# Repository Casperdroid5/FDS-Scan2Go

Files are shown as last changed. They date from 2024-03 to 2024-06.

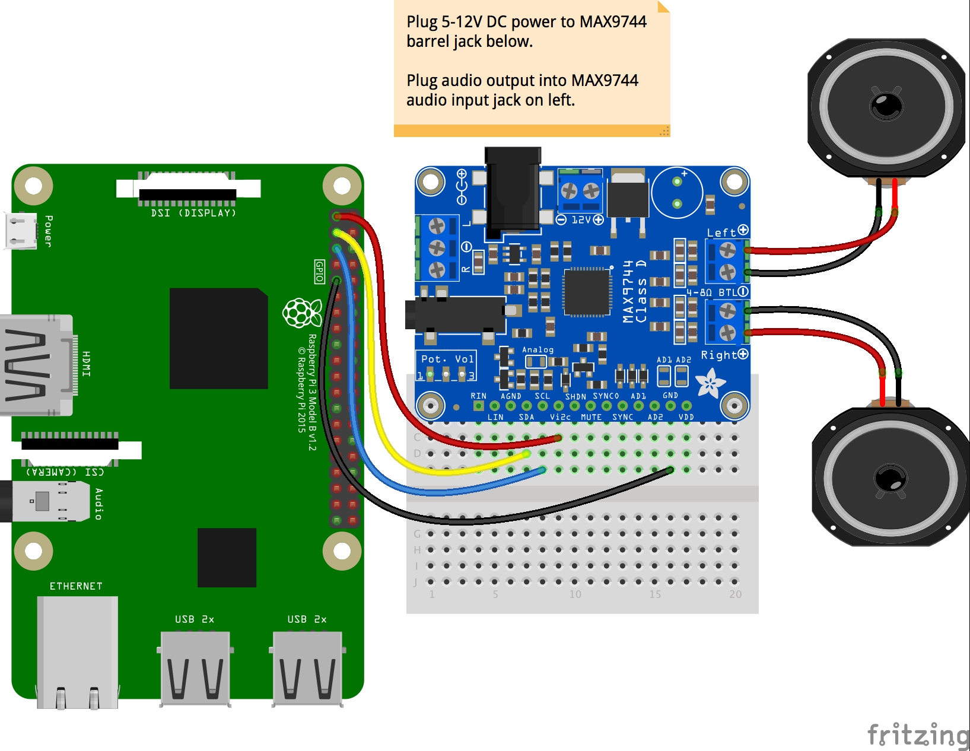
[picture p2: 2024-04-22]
Hardware/Datasheets e.d/adafruit_products_raspi_max9744_i2c_bb.jpg

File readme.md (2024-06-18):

# FDS-Scan2Go

## Overview
The Ferrous Metal Detection Gate (FDS) is a sophisticated system designed to enhance safety for MRI room access by detecting ferrous metals. This system utilizes a Raspberry Pi Pico and Raspberry Pi 5 to facilitate communication with various sensors, providing both auditory and visual feedback to the user.

## Table of Contents
- [Features](#features)
- [Hardware Requirements](#hardware-requirements)
- [Software Setup](#software-setup)
- [Installation](#installation)
  - [Raspberry Pi Pico](#raspberry-pi-pico)
  - [Raspberry Pi 5](#raspberry-pi-5)
- [Usage](#usage)
- [Contributing](#contributing)
- [License](#license)

## Features
- Utilizes a ferrous metal detector for metal detection
- Provides auditory and visual feedback to the user
- Employs both Raspberry Pi Pico and Raspberry Pi 5
- Communicates with multiple sensors for enhanced detection accuracy

## Hardware Requirements
### Raspberry Pi Pico
- All the wanted peripherals (buttons, sensors etc.)
- Micro usb cable (ensure it has data wires)

### Raspberry Pi 5
- Raspberry Pi 25W, power supply
- USB to 3.5mm audio adapter
- Display/monitor for imageoutput
- MicroHDMI to HDMI adapter 

## Software Setup
### Prerequisites
- Python 3.12 or higher
- Required Python libraries (listed in `requirements_rpi5.txt` for Raspberry Pi 5)
- MicroPython libraries for Raspberry Pi Pico (listed in `requirements_pico.txt`)

## Installation
### Raspberry Pi Pico

1. **Install Dependencies**
   Since the Pico runs on MicroPython for this project, you'll need to upload the required libraries manually or use a tool like `mpremote`.

   ```sh
   mpremote mip install micropython-neopixel micropython-machine micropython-time micropython-i2c micropython-uart
   ```

2. **Upload Scripts to Pico**
   Upload the relevant `.py` files to the Pico:
   ```sh
   mpremote fs cp hardware_s2g.py :hardware_s2g.py
   mpremote fs cp system_utils.py :system_utils.py
   mpremote fs cp main.py :main.py
   ```

### Raspberry Pi 5
1. **Prepare MicroSD Card**
   Install Raspbian 64-bit (with desktop) on a 32GB MicroSD card (using Raspberry Pi Imager, for example). Once installed, boot the Raspberry Pi 5, connect it to the internet, and open a terminal with root permissions.

2. **Install Python Dependencies**
   ```sh
   pip install -r requirements_rpi5.txt
   ```

3. **Install System Dependencies**
   ```sh
   sudo apt-get update
   sudo apt-get install feh vlc
   ```

4. **Run the Application**
   Navigate to the project directory and start the main script:
   ```sh
   python main.py
   ```

## Usage
1. **Connect the Raspberry Pi Pico and Raspberry Pi 5 via a MicroUSB cable.**
2. **Start the `main.py` script on the Raspberry Pi 5.**
3. The system will initialize, and the sensors will begin to monitor for ferrous metals. The NeoPixel LEDs and the display will provide feedback based on the detection status.

## Contributing
We welcome contributions to the FDS-Scan2Go project. If you would like to contribute, please fork the repository and submit a pull request. 

If you would like to emplement this code into your own project, ensure to give credit to the original author and mention any significant changes or improvements.

## Disclaimer
This project is licensed under the MIT License. See the [DISCLAIMER](/Software/DISCLAIMER.md) file for more details.

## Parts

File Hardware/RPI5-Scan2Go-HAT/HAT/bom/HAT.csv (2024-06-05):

'Reference' | 'Value' | 'Datasheet' | 'Footprint' | 'Qty' | 'Mouser' | 'Description' | 'Farnell'
'C1' | '0.1uF' | 'https://nl.mouser.com/datasheet/2/40/cx5r-2835979.pdf' | 'Capacitor_SMD:C_1206_3216Metric_Pad1.33x1.80mm_HandSolder' | '1' | '581-12066D104KAT4A ' | 'Unpolarized capacitor' | ''
'D1' | '5.0V' | 'https://www.bourns.com/docs/product-datasheets/smbj.pdf?sfvrsn=34552159_17' | 'SamacSys_Parts:DIOM5436X261N' | '1' | '652-SMBJ26A ' | '' | ''
'D2' | 'WS2812B' | 'https://cdn-shop.adafruit.com/datasheets/WS2812B.pdf' | 'LED_SMD:LED_WS2812B_PLCC4_5.0x5.0mm_P3.2mm' | '1' | ' 474-COM-16346 ' | 'RGB LED with integrated controller' | ''
'F1' | '5 A' | 'https://nl.mouser.com/datasheet/2/54/Bourns_01_26_2024_SF_1206S_R_Datasheet-3398014.pdf' | 'Fuse:Fuse_2010_5025Metric_Pad1.52x2.65mm_HandSolder' | '1' | '652-SF-1206HH1000R-2 ' | '' | ''
'IC1' | 'MC14043BDR2G' | 'https://www.onsemi.com/pub/Collateral/MC14043B-D.PDF' | 'SamacSys_Parts:SOIC127P600X175-16N' | '1' | '863-MC14043BDR2G' | 'ON SEMICONDUCTOR - MC14043BDR2G - SR-LATCH, QUAD, TRI-STATE, SOIC-16' | ''
'J1' | 'RPi_GPIO' | 'https://nl.mouser.com/datasheet/2/813/12313-1074847.pdf' | '_custom:Pin_Header_Straight_2x20' | '1' | '474-PRT-14017 ' | '' | ''
'J2' | 'Conn_01x02_Socket' | '~' | 'Connector_JST:JST_EH_B2B-EH-A_1x02_P2.50mm_Vertical' | '1' | '' | 'Generic connector, single row, 01x02, script generated' | ' 2399159 '
'J3' | 'Conn_01x14_Socket' | '~' | 'Connector_PinSocket_2.54mm:PinSocket_1x14_P2.54mm_Vertical' | '1' | '' | 'Generic connector, single row, 01x14, script generated' | ''
'J4' | 'Conn_01x03_Socket' | '~' | 'Connector_JST:JST_EH_B3B-EH-A_1x03_P2.50mm_Vertical' | '1' | '' | 'Generic connector, single row, 01x03, script generated' | ' 2399161 '
'J5' | 'Conn_01x03_Socket' | '~' | 'Connector_JST:JST_EH_B3B-EH-A_1x03_P2.50mm_Vertical' | '1' | '' | 'Generic connector, single row, 01x03, script generated' | ' 2399161 '
'J6' | 'Conn_01x03_Socket' | '~' | 'Connector_JST:JST_EH_B3B-EH-A_1x03_P2.50mm_Vertical' | '1' | '' | 'Generic connector, single row, 01x03, script generated' | ' 2399161 '
'J7' | 'Conn_01x04_Socket' | '~' | 'Connector_JST:JST_EH_B4B-EH-A_1x04_P2.50mm_Vertical' | '1' | '' | 'Generic connector, single row, 01x04, script generated' | '1830714'
'J8' | 'Conn_01x02_Socket' | '~' | 'Connector_JST:JST_EH_B2B-EH-A_1x02_P2.50mm_Vertical' | '1' | '' | 'Generic connector, single row, 01x02, script generated' | ' 2399159 '
'J9' | 'Conn_01x02_Socket' | '~' | 'Connector_JST:JST_EH_B2B-EH-A_1x02_P2.50mm_Vertical' | '1' | '' | 'Generic connector, single row, 01x02, script generated' | ' 2399159 '
'J10' | 'Conn_01x02_Socket' | '~' | 'Connector_JST:JST_EH_B2B-EH-A_1x02_P2.50mm_Vertical' | '1' | '' | 'Generic connector, single row, 01x02, script generated' | ' 2399159 '
'J12' | 'Conn_01x02_Socket' | '~' | 'Connector_JST:JST_EH_B2B-EH-A_1x02_P2.50mm_Vertical' | '1' | '' | 'Generic connector, single row, 01x02, script generated' | ' 2399159 '
'J13' | 'Conn_01x02_Socket' | '~' | 'Connector_JST:JST_EH_B2B-EH-A_1x02_P2.50mm_Vertical' | '1' | '' | 'Generic connector, single row, 01x02, script generated' | ' 2399159 '
'J14' | 'Conn_01x02_Socket' | '~' | 'Connector_JST:JST_EH_B2B-EH-A_1x02_P2.50mm_Vertical' | '1' | '' | 'Generic connector, single row, 01x02, script generated' | ' 2399159 '
'J15' | 'Jack-DC 5V' | 'https://nl.farnell.com/cliff-electronic-components/fcr681466p/dc-barrel-conn-jack-2-1mm-2-5mm/dp/2759202' | 'Connector_BarrelJack:BarrelJack_Wuerth_6941xx301002' | '1' | '' | '' | 'FCR681466P'
'J16' | 'Conn_01x03_Socket' | '~' | 'Connector_JST:JST_EH_B3B-EH-A_1x03_P2.50mm_Vertical' | '1' | '' | 'Generic connector, single row, 01x03, script generated' | ' 2399161 '
'J18' | 'Conn_01x02_Socket' | '~' | 'Connector_JST:JST_EH_B2B-EH-A_1x02_P2.50mm_Vertical' | '1' | '' | 'Generic connector, single row, 01x02, script generated' | ' 2399159 '
'J19' | 'Conn_01x02_Socket' | '~' | 'Connector_JST:JST_EH_B2B-EH-A_1x02_P2.50mm_Vertical' | '1' | '' | 'Generic connector, single row, 01x02, script generated' | ' 2399159 '
'J20' | 'Conn_01x05_Socket' | '~' | 'Connector_JST:JST_EH_B5B-EH-A_1x05_P2.50mm_Vertical' | '1' | '' | 'Generic connector, single row, 01x05, script generated' | '1830716 '
'J21' | 'Conn_01x05_Socket' | '~' | 'Connector_JST:JST_EH_B5B-EH-A_1x05_P2.50mm_Vertical' | '1' | '' | 'Generic connector, single row, 01x05, script generated' | '1830716 '
'J22' | 'Conn_01x02_Socket' | '~' | 'Connector_JST:JST_EH_B2B-EH-A_1x02_P2.50mm_Vertical' | '1' | '' | 'Generic connector, single row, 01x02, script generated' | ' 2399159 '
'J23' | 'Conn_01x04_Socket' | '~' | 'Connector_JST:JST_EH_B4B-EH-A_1x04_P2.50mm_Vertical' | '1' | '' | 'Generic connector, single row, 01x04, script generated' | '1830714'
'J24' | 'Conn_01x02_Socket' | '~' | 'Connector_JST:JST_EH_B2B-EH-A_1x02_P2.50mm_Vertical' | '1' | '' | 'Generic connector, single row, 01x02, script generated' | ' 2399159 '
'JP1' | 'Jumper_2_Open' | '~' | 'Jumper:SolderJumper-2_P1.3mm_Open_TrianglePad1.0x1.5mm' | '1' | '' | 'Jumper, 2-pole, open' | ''
'JP2' | 'Jumper_2_Open' | '~' | 'Jumper:SolderJumper-2_P1.3mm_Open_TrianglePad1.0x1.5mm' | '1' | '' | 'Jumper, 2-pole, open' | ''
'R1' | '10K' | '~' | 'Resistor_SMD:R_1206_3216Metric_Pad1.30x1.75mm_HandSolder' | '1' | '' | 'Resistor' | '3545485 '
'R2' | '10K' | '~' | 'Resistor_SMD:R_1206_3216Metric_Pad1.30x1.75mm_HandSolder' | '1' | '' | 'Resistor' | '3545485 '
'TP1' | 'TestPoint' | '~' | 'TestPoint:TestPoint_Pad_2.0x2.0mm' | '1' | '' | 'test point' | ''
'U1' | 'Pico' | 'https://nl.mouser.com/datasheet/2/635/pico_datasheet-3048936.pdf' | 'MCU_RaspberryPi_and_Boards:RPi_Pico_SMD_TH' | '1' | '358-SC0915 ' | '' | ''
'U2' | 'LM741' | 'http://www.ti.com/lit/ds/symlink/lm741.pdf' | 'Package_SO:SOIC-8_3.9x4.9mm_P1.27mm' | '1' | '' | 'Operational Amplifier, DIP-8/TO-99-8' | '3117118 '

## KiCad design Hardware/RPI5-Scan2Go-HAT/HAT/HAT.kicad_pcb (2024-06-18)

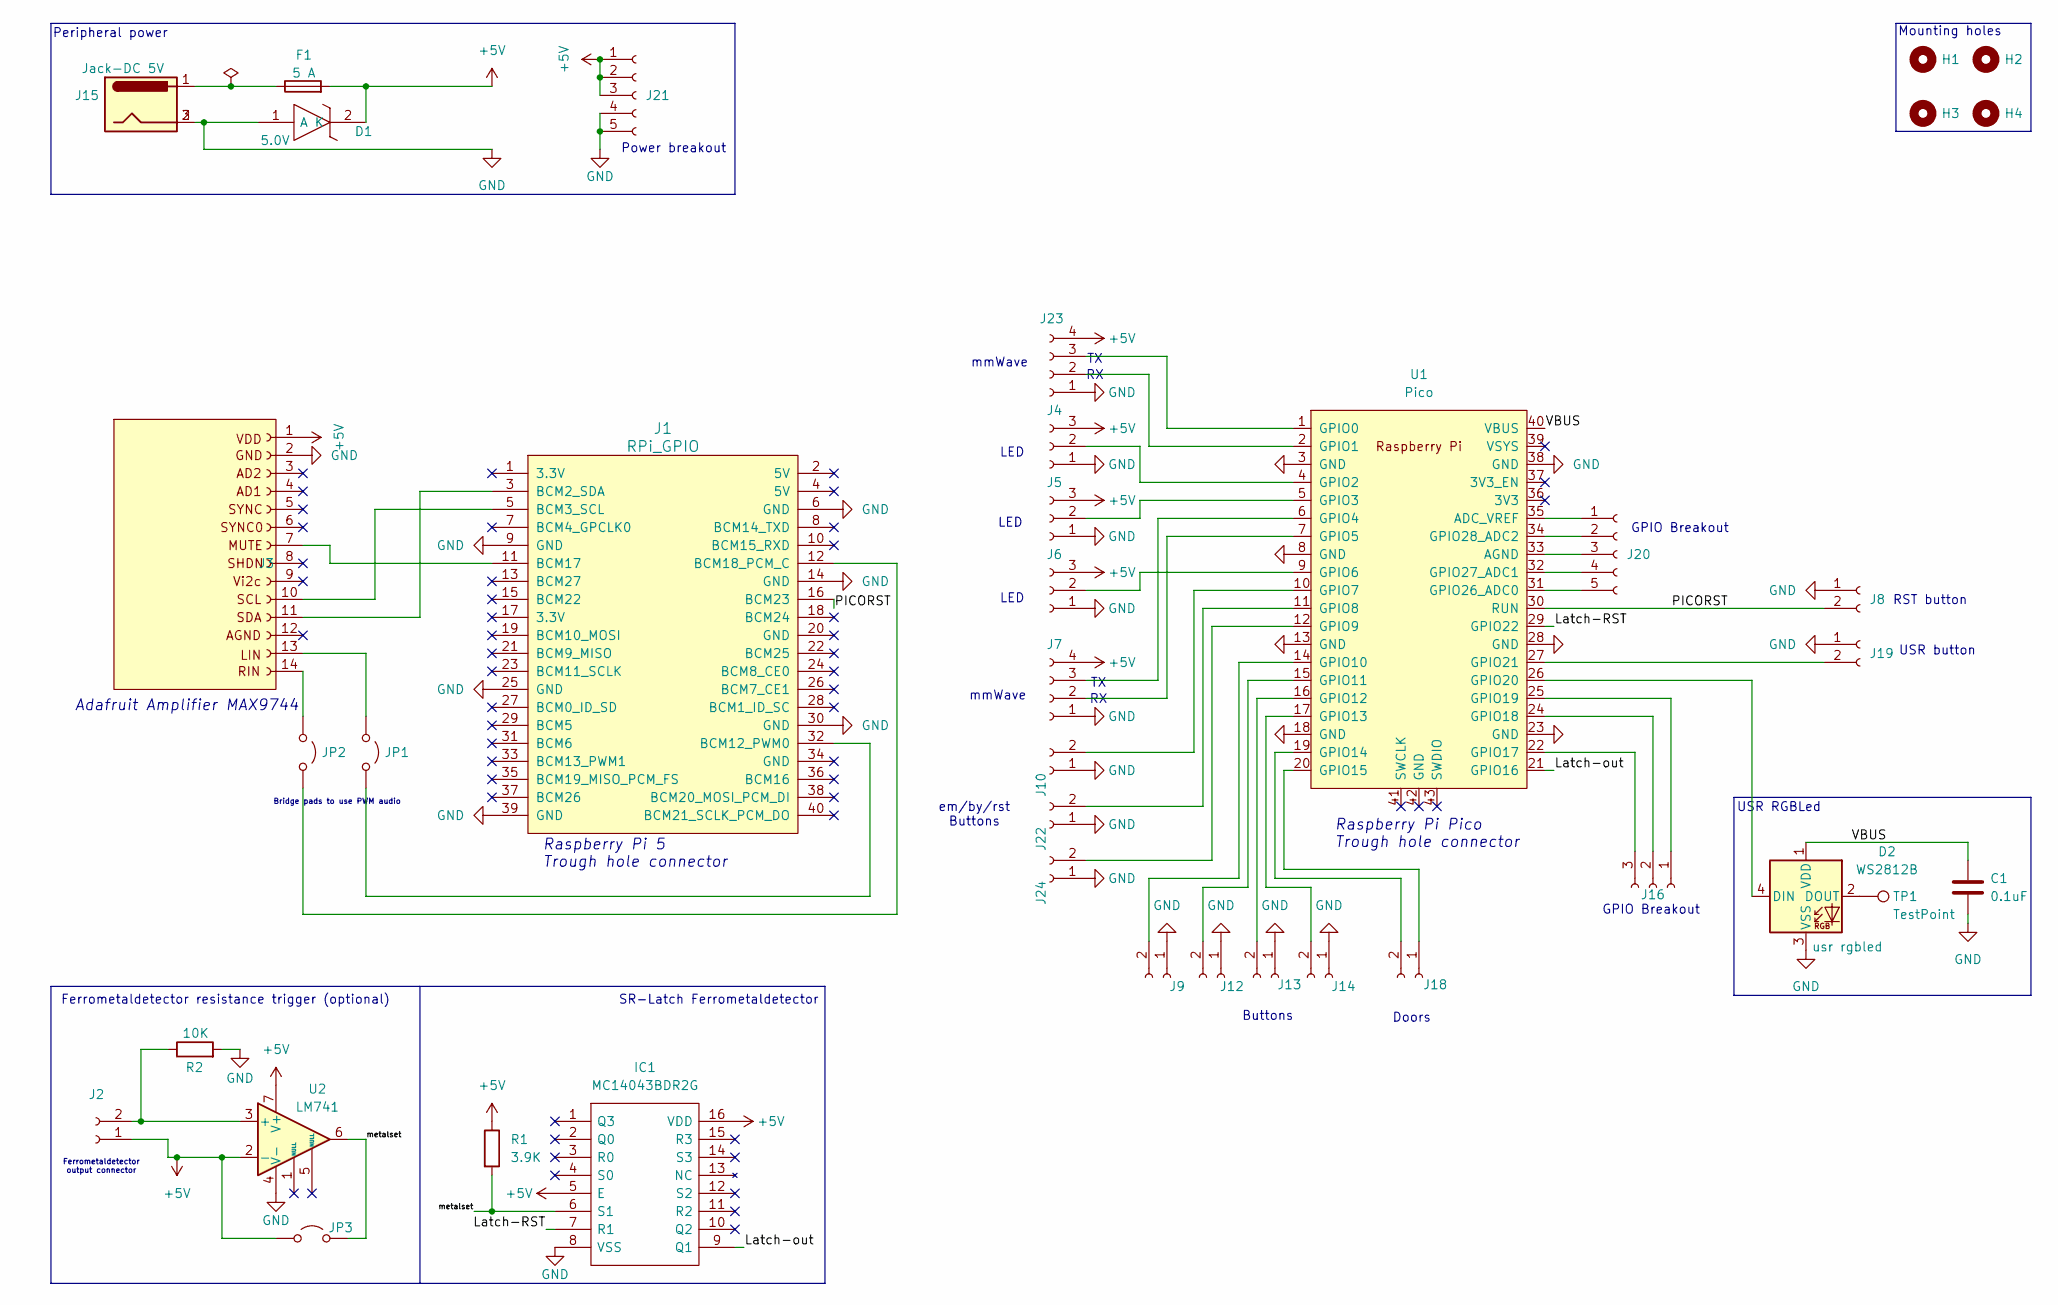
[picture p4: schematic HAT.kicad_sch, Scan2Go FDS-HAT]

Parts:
C1: 0.1uF; C_1206_3216Metric_Pad1.33x1.80mm_HandSolder; Mouser 581-12066D104KAT4A
D1: 5.0V; DIOM5436X261N; LCSC C10216
D2: WS2812B; LED_WS2812B_PLCC4_5.0x5.0mm_P3.2mm; Mouser 474-COM-16346
F1: 5 A; Fuse_2010_5025Metric_Pad1.52x2.65mm_HandSolder; LCSC C136353
H1, H2, H3, H4: MountingHole; MountingHole_3.2mm_M3
IC1: MC14043BDR2G; SOIC127P600X175-16N; Mouser Part Number 863-MC14043BDR2G
J1: RPi_GPIO; Pin_Header_Straight_2x20; Mouser 474-PRT-14017
J2, J8, J9, J10, J12, J13, J14, J18, J19, J22, J24: Conn_01x02_Socket; JST_EH_B2B-EH-A_1x02_P2.50mm_Vertical; Farnell 2399159
J3: Conn_01x14_Socket; PinSocket_1x14_P2.54mm_Vertical
J4, J5, J6, J16: Conn_01x03_Socket; JST_EH_B3B-EH-A_1x03_P2.50mm_Vertical; Farnell 2399161
J7, J23: Conn_01x04_Socket; JST_EH_B4B-EH-A_1x04_P2.50mm_Vertical; Farnell 1830714
J15: Jack-DC 5V; BarrelJack_Wuerth_6941xx301002; Farnell FCR681466P
J20, J21: Conn_01x05_Socket; JST_EH_B5B-EH-A_1x05_P2.50mm_Vertical; Farnell 1830716
JP1, JP2, JP3: Jumper_2_Open; SolderJumper-2_P1.3mm_Open_TrianglePad1.0x1.5mm
R1: 3.9K; R_1206_3216Metric_Pad1.30x1.75mm_HandSolder; Farnell 3545485
R2: 10K; R_1206_3216Metric_Pad1.30x1.75mm_HandSolder; Farnell 3545485
TP1: TestPoint; TestPoint_Pad_2.0x2.0mm
U1: Pico; RPi_Pico_SMD_TH; Mouser 358-SC0915
U2: LM741; SOIC-8_3.9x4.9mm_P1.27mm; Farnell 3117118

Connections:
+5V: D1.2 (K), F1.2, IC1.5 (E), IC1.16 (VDD), J2.1, J3.1 (VDD), J4.3, J5.3, J6.3, J7.4, J21.1, J21.2, J21.3, J23.4, JP3.1 (A), R1.1, U2.2 (-), U2.7 (V+)
/Latch-RST: IC1.7 (R1), U1.29 (GPIO22)
/Latch-out: IC1.9 (Q1), U1.21 (GPIO16)
/PICORST: J1.16 (BCM23), J8.2, U1.30 (RUN)
/VBUS: C1.1, D2.1 (VDD), U1.40 (VBUS)
/metalset: IC1.6 (S1), JP3.2 (B), R1.2, U2.6
GND: C1.2, D1.1 (A), D2.3 (VSS), IC1.8 (VSS), J1.6 (GND), J1.9 (GND), J1.14 (GND), J1.25 (GND), J1.30 (GND), J1.39 (GND), J3.2 (GND), J4.1, J5.1, J6.1, J7.1, J8.1, J9.1, J10.1, J12.1, J13.1, J14.1, J15.2, J15.3, J19.1, J21.4, J21.5, J22.1, J23.1, J24.1, R2.2, U1.3 (GND), U1.8 (GND), U1.13 (GND), U1.18 (GND), U1.23 (GND), U1.28 (GND), U1.38 (GND), U2.4 (V-)
unnamed: D2.4 (DIN), U1.26 (GPIO20)
unnamed: D2.2 (DOUT), TP1.1
unnamed: F1.1, J15.1
unnamed: J1.3 (BCM2_SDA), J3.11 (SDA)
unnamed: J1.5 (BCM3_SCL), J3.10 (SCL)
unnamed: J1.32 (BCM12_PWM0), JP1.2 (B)
unnamed: J1.11 (BCM17), J3.7 (MUTE)
unnamed: J1.12 (BCM18_PCM_C), JP2.2 (B)
unnamed: J2.2, R2.1, U2.3 (+)
unnamed: J3.13 (LIN), JP1.1 (A)
unnamed: J3.14 (RIN), JP2.1 (A)
unnamed: J4.2, U1.4 (GPIO2)
unnamed: J5.2, U1.5 (GPIO3)
unnamed: J6.2, U1.9 (GPIO6)
unnamed: J7.2, U1.7 (GPIO5)
unnamed: J7.3, U1.6 (GPIO4)
unnamed: J9.2, U1.14 (GPIO10)
unnamed: J10.2, U1.10 (GPIO7)
unnamed: J12.2, U1.15 (GPIO11)
unnamed: J13.2, U1.16 (GPIO12)
unnamed: J14.2, U1.17 (GPIO13)
unnamed: J16.1, U1.25 (GPIO19)
unnamed: J16.2, U1.24 (GPIO18)
unnamed: J16.3, U1.22 (GPIO17)
unnamed: J18.1, U1.20 (GPIO15)
unnamed: J18.2, U1.19 (GPIO14)
unnamed: J19.2, U1.27 (GPIO21)
unnamed: J20.1, U1.35 (ADC_VREF)
unnamed: J20.2, U1.34 (GPIO28_ADC2)
unnamed: J20.3, U1.33 (AGND)
unnamed: J20.4, U1.32 (GPIO27_ADC1)
unnamed: J20.5, U1.31 (GPIO26_ADC0)
unnamed: J22.2, U1.11 (GPIO8)
unnamed: J23.2, U1.2 (GPIO1)
unnamed: J23.3, U1.1 (GPIO0)
unnamed: J24.2, U1.12 (GPIO9)

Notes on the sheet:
mmWave
Adafruit Amplifier MAX9744
LED
Bridge pads to use PWM audio
USR button
Buttons
GPIO Breakout
RST button
Doors
Raspberry Pi Pico Trough hole connector
Mounting holes
Ferrometaldetector resistance trigger (optional)
USR RGBLed
Peripheral power
Raspberry Pi 5 Trough hole connector
em/by/rst Buttons
SR-Latch Ferrometaldetector
Ferrometaldetector output connector
Power breakout

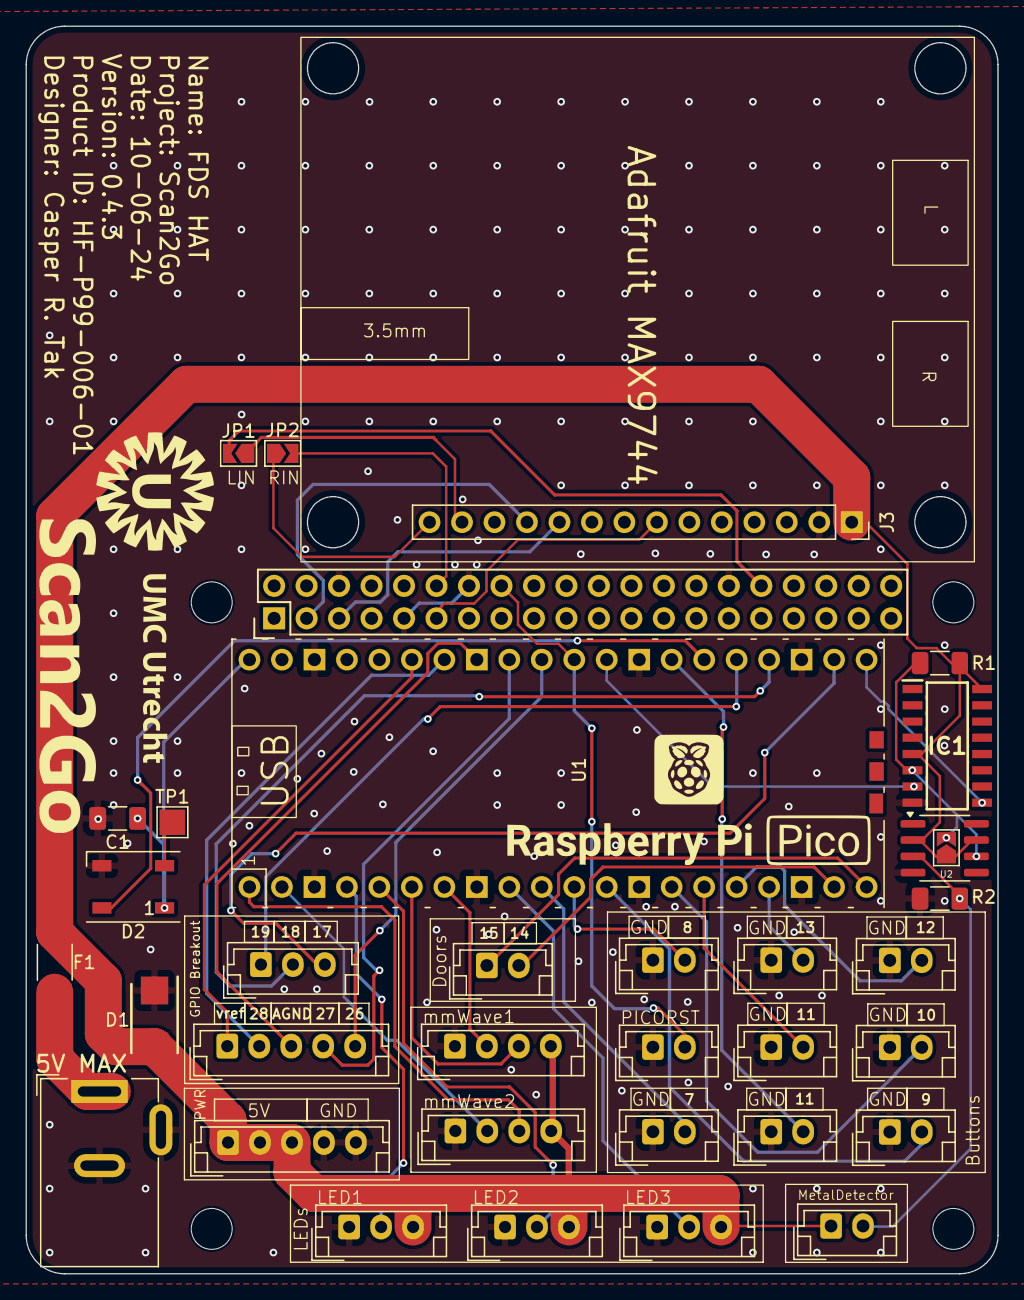
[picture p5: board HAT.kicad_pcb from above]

Board: 2 copper layers, 76.0 x 97.6 mm, 39 parts (0 on the bottom side), 43 nets.

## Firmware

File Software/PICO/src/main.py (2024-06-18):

from hardware_s2g import LD2410PERSONDETECTOR, DOOR, WS2812
from system_utils import SystemInitCheck, Timer, USBCommunication, Log
from machine import Pin
import time

global running   # system running global variable
running = False  # wait for system to be initialised before starting the state machine

class StateMachine:

    def __init__(self):

        # StatemachineVariables
        self.state = None
        self.user_in_mri = False
        self.emergency_state_triggerd = False
        self.system_initialised = False
        self.system_override_state_triggerd = False
        self.user_returned_from_mri = False
        self.audio_played = False 
        self.image_opened = False
        self.RPI5connected = False
        self.messagecounter = 0
        
        # Sensor thresholds
        self.sensor_to_object_distance_threshold = 180 # distance threshold for person detection in cm
        
        # Define integer constants for states
        self.INITIALISATION_STATE = 0
        self.USER_FIELD_A_RESPONSE_STATE = 1
        self.USER_FIELD_B_RESPONSE_STATE = 2
        self.USER_IN_MR_ROOM_STATE = 3
        self.USER_RETURNS_FROM_MR_ROOM_STATE = 4
        self.USER_EXITS_FDS_STATE = 5

        # Initialize indicator lights
        self.LEDStrip_mmWave_fieldA = WS2812(pin_number=2, num_leds=2, brightness=50)  # brigness is a value between 1 and 100
        self.LEDStrip_mmWave_fieldB = WS2812(pin_number=3, num_leds=2, brightness=50)
        self.LEDStrip_FerrometalDetector = WS2812(pin_number=6, num_leds=2, brightness=50)
        self.LEDStrip_fieldA = WS2812(pin_number=7, num_leds=48, brightness=50)
        self.LEDStrip_fieldB = WS2812(pin_number=8, num_leds=48, brightness=50)
        self.BoardLED = WS2812(pin_number=20, num_leds= 1, brightness= 30)

        # Initialize persondetectors
        self.mmWave_fieldB = LD2410PERSONDETECTOR(uart_number=0, baudrate=256000, tx_pin=0, rx_pin=1)
        self.mmWave_fieldA = LD2410PERSONDETECTOR(uart_number=1, baudrate=256000, tx_pin=4, rx_pin=5)

        # Initialize doors
        self.door_changeroom = DOOR(pin_number=14, angle_closed=90, angle_open=0, position_sensor_pin=19)
        self.door_mri_room = DOOR(pin_number=15, angle_closed=90, angle_open=185, position_sensor_pin=21)

        # Initialize buttons
        self.button_emergency = Pin(10, Pin.IN, Pin.PULL_UP)  # Emergency situation button
        self.button_emergency.irq(trigger=Pin.IRQ_FALLING, handler=self.IRQ_handler_emergencybutton_press)
        self.button_system_bypass = Pin(13, Pin.IN, Pin.PULL_UP)  # System override button
        self.button_system_bypass.irq(trigger=Pin.IRQ_FALLING, handler=self.IRQ_handler_bypassbutton_press)
        self.button_system_reset = Pin(17, Pin.IN, Pin.PULL_UP) # System bypass button
        self.button_system_reset.irq(trigger=Pin.IRQ_FALLING, handler= self.IRQ_handler_button_system_reset)
        #self.button_door_changeroom = Pin(X, Pin.IN, Pin.PULL_UP)  # Door 1 button (open door)
        #self.button_door_changeroom.irq(trigger=Pin.IRQ_FALLING, handler=self.IRQ_handler_door_changeroom_button_press)
        #self.button_door_mri_room = Pin(X, Pin.IN, Pin.PULL_UP)  # Door 2 button (open door)
        #self.button_door_mri_room.irq(trigger=Pin.IRQ_FALLING, handler=self.IRQ_handler_door_mri_room_button_press)

        # Initialize ferrometal detector input and latch reset
        self.ferrometaldetectorinput = Pin(16, Pin.IN, Pin.PULL_UP) # Ferrometal detector input pin
        self.latchreset = Pin(22, Pin.OUT) # reset latch pin

        # Initialize UART-communication with RPI5 over USB
        self.RPI5_USB_LINE = USBCommunication()

        # Initialize a timer
        self.timer1 = Timer()  
        self.timer1.start_timer()

    def IRQ_handler_door_changeroom_button_press(self, pin):
        if self.state == self.USER_FIELD_A_RESPONSE_STATE:
            if self.door_changeroom.door_state == "closed":
                self.door_changeroom.open_door() 

    def IRQ_handler_door_mri_room_button_press(self, pin):
        if self.state == self.USER_IN_MR_ROOM_STATE or (self.ferrometaldetectorinput.value() == 0 and self.user_returned_from_mri) or self.user_in_mri:
            if self.door_mri_room.door_state == "closed":
                self.door_mri_room.open_door()  

    def IRQ_handler_emergencybutton_press(self, pin):
        self.RPI5_USB_LINE.send_message("Emergency button") 
        self.RPI5_USB_LINE.send_message("showimage 7") # emergency situation image
        systemlog.log_message("Emergency button pressed")
        self.emergency_state_triggerd = True
        global running
        running = False # stop the state machine

    def IRQ_handler_button_system_reset(self, pin):
        self.RPI5_USB_LINE.send_message("System reset button")
        systemlog.log_message("System reset button pressed")
        self.system_initialised = False
        self.system_override_state_triggerd = False
        self.emergency_state_triggerd = False
        self.state = self.INITIALISATION_STATE
        global running 
        running = True # start the state machine

    def IRQ_handler_bypassbutton_press(self, pin):
        self.RPI5_USB_LINE.send_message("Override button pressed")
        self.RPI5_USB_LINE.send_message("showimage 8") # system override image 
        systemlog.log_message("System override button pressed")
        self.emergency_state_triggerd = False
        self.system_override_state_triggerd = not self.system_override_state_triggerd # toggle system override state
        global running
        running = False # stop the state machine

    def person_detected_in_field(self, field): 

        if field == 'A':
            if self.mmWave_fieldA.scan_for_people() and self.mmWave_fieldA.get_detection_distance() < self.sensor_to_object_distance_threshold:
                self.LEDStrip_mmWave_fieldA.set_color("green") 
                return True
            else:
                self.LEDStrip_mmWave_fieldA.set_color("red")
                return False
        elif field == 'B':
            if self.mmWave_fieldB.scan_for_people() and self.mmWave_fieldB.get_detection_distance() < self.sensor_to_object_distance_threshold:
                self.LEDStrip_mmWave_fieldB.set_color("green")
                return True
            else:
                self.LEDStrip_mmWave_fieldB.set_color("red")
                return False

    def RPI5healthchecker(self):
        self.RPI5connected = False
        self.timer1.reset()
        self.messagecounter = 0
        current_time = 0

        while not self.RPI5connected: 
            current_time = self.timer1.get_time()
            
            if 0 < current_time < 50:
                self.BoardLED.set_color("white")
                if self.messagecounter < 1:
                    self.RPI5_USB_LINE.send_message("stillalivemessage")
                    self.messagecounter += 1              
            elif 100 < current_time < 1000:
                if self.messagecounter < 2:
                    self.RPI5_USB_LINE.send_message("stillalivemessage")
                    self.messagecounter += 1              
            elif 2000 < current_time < 5000:
                if self.messagecounter < 3:
                    self.RPI5_USB_LINE.send_message("stillalivemessage")
                    self.messagecounter += 1

            if self.RPI5_USB_LINE.receive_message():
                print("RPI5 is still alive")
                self.RPI5_USB_LINE.send_message("stillalive")
                self.BoardLED.set_color("green")
                self.RPI5connected = True
            
            if 5000 < current_time < 10000 and self.messagecounter == 3: # if RPI5 does not respond after 10 seconds, shut down the system
                systemlog.log_message("Failed to communicate with RPI5, shutting down system")
                self.BoardLED.set_color("red")
                exit(1)


    def systemset(self):     
            self.LEDStrip_mmWave_fieldA.off()
            self.LEDStrip_mmWave_fieldB.off()
            self.LEDStrip_FerrometalDetector.off() 
            self.RPI5healthchecker()
            self.LEDStrip_fieldA.off()
            self.LEDStrip_fieldB.off()
            self.door_mri_room.close_door()  
            self.door_changeroom.open_door()  
            self.system_initialised = True
            self.RPI5_USB_LINE.send_message("System initialised")
            self.RPI5_USB_LINE.send_message("playaudio 1") # system initialised audio
            time.sleep(2) # wait for audio to finish playing  

    def run(self): # State machine logic

        global running 
        self.state = self.INITIALISATION_STATE # default state when statemachine is started

        while running: 
            if self.state == self.INITIALISATION_STATE:
                if self.system_initialised == False:
                    self.systemset()
                elif not self.image_opened:
                    self.RPI5_USB_LINE.send_message("showimage 0")
                    self.image_opened = True
                elif not self.audio_played :
                    self.RPI5_USB_LINE.send_message("playaudio 4")  
                    self.audio_played = True   
                    self.RPI5healthchecker()
                elif self.person_detected_in_field('A') == False and self.person_detected_in_field('B') == False:
                    self.LEDStrip_fieldA.off()
                    self.LEDStrip_fieldB.off()
                    self.RPI5_USB_LINE.send_message("closeimage") # close all images
                    self.latchreset.value(1) # clear/reset the metal detector latch
                    self.audio_played = False 
                    self.image_opened = False
                    self.latchreset.value(0)
                    self.door_changeroom.open_door()
                    self.RPI5healthchecker()
                    self.state = self.USER_FIELD_A_RESPONSE_STATE

            elif self.state == self.USER_FIELD_A_RESPONSE_STATE:
                if not self.audio_played:
                    self.RPI5_USB_LINE.send_message("playaudio 5") # move to field A audio 
                    self.audio_played = True  
                    self.LEDStrip_fieldA.set_color("white")
                if not self.image_opened:
                    self.RPI5_USB_LINE.send_message("showimage 1")  # move to field A image
                    self.image_opened = True
                if self.person_detected_in_field('A') == True and self.person_detected_in_field('B') == False: 
                    self.door_changeroom.close_door()
                    self.RPI5_USB_LINE.send_message("showimage 2") # move to field B image
                    self.RPI5_USB_LINE.send_message("playaudio 6") # move to field B audio
                    self.audio_played = False 
                    self.image_opened = False
                    self.LEDStrip_fieldA.off()
                    self.LEDStrip_fieldB.set_color("white")
                    self.RPI5healthchecker()
                    self.state = self.USER_FIELD_B_RESPONSE_STATE
                elif self.person_detected_in_field('A') == False and self.person_detected_in_field('B') == True: # Wait for user to move to field A
                    self.LEDStrip_fieldA.set_color("white")
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

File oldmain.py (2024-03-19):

#Todo:
    # altijd iets returnen bij een functie
    # functies zo klein mogelijk houden 1 functie = 1 taak
    # geen print statements in de functies
    # geen while True gebruiken
    # time sleep vermijden
    # Alles functioneel, dus liever geen waardes in de code

from machine import Pin, ADC
from hardwares2g import RGB, DOOR
import time

button_pins = [9, 16, 17, 18] # Pins for the interruptbuttons

def _on_button_pressed(pin):
    button_number = pin
    print("Button", button_number, "was pressed")

for pin in button_pins:
    button = Pin(pin, Pin.IN, Pin.PULL_UP)
    button.irq(trigger=Pin.IRQ_FALLING, handler=_on_button_pressed)

class StateMachine:
    def __init__(self):

        # Variables 
        self.AngleOpen = 0 
        self.AngleClosed = 90
        self.ferrometal_detected = False
        self.user_returned_from_mri = False
        
        # Define integer constants for states
        self.INITIALISATION_STATE = 0
        self.WAIT_FOR_USER_FIELD_A_STATE = 1
        self.WAIT_FOR_USER_FIELD_B_STATE = 2
        self.FERROMETAL_DETECTION_STATE = 3
        self.UNLOCK_AND_OPEN_DOOR1_STATE = 4
        self.LOCK_AND_CLOSE_DOOR1_STATE = 5
        self.UNLOCK_AND_OPEN_DOOR2_STATE = 6
        self.LOCK_AND_CLOSE_DOOR2_STATE = 7
        self.EMERGENCY_STATE = 8

        # Initialize hardware components
        self.Door2LockState = RGB(10, 11, 12)
        self.Door1LockState = RGB(2, 3, 4)
        self.FerroDetectLED = RGB(6, 7, 8)
        self.Door1 = DOOR(14, self.AngleClosed, self.AngleOpen)
        self.Door2 = DOOR(15, self.AngleClosed, self.AngleOpen)
        self.Pot1 = ADC(27)
        self.field_a = Pin(18, Pin.IN, Pin.PULL_UP)
        self.field_b = Pin(17, Pin.IN, Pin.PULL_UP)
        self.emergencybutton = Pin(5, Pin.IN, Pin.PULL_UP)
        self.emergencybutton.irq(trigger=Pin.IRQ_FALLING, handler=self.on_press_emergency_button)

    def delayed_print(self, message, delay):
        print(message)
        time.sleep(delay)

# State Functions
    def initialisation_state(self):
        self.Door1LockState.off() # Turn indicator off
        self.Door2LockState.off() # Turn indicator off
        self.FerroDetectLED.off() # Turn indicator off
        self.delayed_print("Initialisation state", 1)
        self.Door2._close_door() # _close_door DOOR 2
        self.Door2LockState.set_color("red") # DOOR Locked
        self.Door1._open_door() # _open_door DOOR 1
        self.Door1LockState.set_color("green")  # DOOR Unlocked
        return self.WAIT_FOR_USER_FIELD_A_STATE

    def user_field_a_response_state(self):
        self.delayed_print("Waiting for user field A state",1)
        if self.field_a.value() == True and self.field_b.value() == False: 
            if self.user_returned_from_mri == False and self.ferrometal_detected == False:
                return self.LOCK_AND_CLOSE_DOOR1_STATE 
            elif self.user_returned_from_mri: 
                return self.UNLOCK_AND_OPEN_DOOR1_STATE
        else: 
            return self.WAIT_FOR_USER_FIELD_A_STATE
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

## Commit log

2024-02-26 functional code for button and rgb led + tests
2024-02-27 created led and led test
2024-02-27 renamed LED class to pwm
2024-02-27 finished creating objects and pin assignment
2024-02-29 added servo code and test code
2024-02-29 servo code now passes position.
2024-03-05 improved Niveau 3, broke scan LED
2024-03-05 fixed servo class
2024-03-07 fixed up wiring issues in code
2024-03-12 replaced oled with print
2024-03-12 statemachine seems to function (LEDS work)
2024-03-13 chainged file names. added led and door motor
2024-03-14 changed led en door functions
2024-03-14 mmWave sensor UART readout succesfull
2024-03-15 potmeter linked with motor and led and uasyncio
2024-03-18 added second uart input device, improved rgb led test
2024-03-21 statemachine improved, state transitioning with switches (now a wire)
2024-03-26 trying to add uart sensors
2024-03-26 mmWave sensors implemented
2024-03-27 created and implemented WS2812 led class
2024-03-27 trying new door sensors class
2024-03-28 replaced RGB LED with WS2812 in all files
2024-03-28 added set brightness function to led
2024-03-28 restored leds class
2024-03-28 user input via terminal to temporarly replace mmWave sensors (not stable)
2024-03-28 door objects renamed. doorstate sensor values changed
2024-03-29 Added leds for doors
2024-04-02 added super class for door leds and added loggin for buttons.
2024-04-12 new mmWave sensor tested
2024-04-12 changed code to work with rpi pico led
2024-04-15 testcode for mmWave and RGB LED
2024-04-17 moved class, renamed and altered mmwave classes and removed prints.
2024-04-17 improvements on usbcom and printsstatements and working on showing images on rpi5
2024-04-18 detached leds from doors and attached to mmWavesensors.
2024-04-19 minor flow improvements
2024-04-22 trying to fix github again
    [HAT.kicad_pcb, HAT.kicad_sch]
2024-04-22 improved symbols of pico and rpi
    [HAT.kicad_sch]
2024-04-22 created footprint for Adafruit amplifier
    [HAT.kicad_pcb, HAT.kicad_sch]
2024-04-23 started pcb routing
    [HAT.kicad_pcb, HAT.kicad_sch]
2024-04-24 swapped mmWave sensors around, changed mmwave threshold
2024-04-26 added power circuit and improved documentation
    [HAT.kicad_sch]
2024-04-26 schematic finished for now (to be reviewed)
    [HAT.kicad_sch]
2024-04-26 added footprints
    [HAT.kicad_sch]
2024-05-04 added doxygen compatible comments to main
    [HAT.kicad_pcb]
2024-05-13 changed requirements and pcb format
    [HAT.kicad_pcb, HAT.kicad_sch]
2024-05-13 added 3d models to design
    [HAT.kicad_pcb]
2024-05-13 improved layout
    [HAT.kicad_pcb, HAT.kicad_sch]
2024-05-13 started routing
    [HAT.kicad_pcb, HAT.kicad_sch]
2024-05-14 removed 5V from barel to pi and pico
    [HAT.kicad_pcb, HAT.kicad_sch]
2024-05-14 V0.1 of pcb finished (To be reviewed)
    [HAT.kicad_pcb, HAT.kicad_sch]
2024-05-14 Silkscreen improvements and additions
    [HAT.kicad_pcb, HAT.kicad_sch]
2024-05-14 minor improvements
    [HAT.kicad_pcb, HAT.kicad_sch]
2024-05-14 V0.2 Finished
    - added product ID
    - via stitching
    - improved silkscreen
    [HAT.kicad_pcb, HAT.kicad_sch]
2024-05-14 cleanup and added BOM
    [HAT.csv, HAT.kicad_sch]
2024-05-14 added fabrication files
    [HAT.kicad_pcb, designators.csv, positions.csv]
2024-05-14 re-linked 3d models and exported 3d models
    [HAT.csv, HAT.kicad_pcb]
2024-05-14 renamed + cleanup
    [HAT.kicad_pcb]
2024-05-14 added missing pico 3d model
    [HAT.kicad_pcb]
2024-05-21 Updated PCB to v0.2.1, improved docs
    [Functionele specificaties HAT.xlsx, HAT.kicad_pcb, HAT.kicad_sch, Technische specificaties HAT.xlsx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]
2024-05-21 Improved bom file and cleanup
    [Functionele specificaties HAT.xlsx, HAT.csv, HAT.kicad_pcb, HAT.kicad_sch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]
2024-05-21 added V0.3 of pcb (srlatch) and added librarys
    [HAT.csv, HAT.kicad_pcb, HAT.kicad_sch, bom.csv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]
2024-05-21 rewrote FDS code to set an reset SR-latch and read ferrometal input
    [HAT.kicad_sch]
2024-05-21 added v0.3.1
    [HAT.csv, HAT.kicad_pcb, HAT.kicad_sch, bom.csv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]
2024-05-22 improved documentation
    [Functionele specificaties HAT.xlsx, HAT.kicad_pcb, Technische specificaties HAT.xlsx]
2024-05-23 changed pin # for bypass
2024-05-27 main.py upated minor changes to specifications
    [Functionele specificaties HAT.xlsx, Technische specificaties HAT.xlsx]
2024-05-28 latch implemented in software
    [Technische specificaties HAT.xlsx]
2024-05-28 minor improvements to leds
2024-05-29 integration uasyncio for pusling leds
2024-05-29 removed print statement floodign
2024-05-31 keyboard mode FDS (Sensor not working)
2024-05-31 restored to mmwave sensors functionality
2024-06-01 added standard values for baudrate both sensors
2024-06-05 updated PCB design to 0.4
    - added amplifier trigger to schematic and pcb
    [HAT.kicad_pcb, HAT.kicad_sch]
2024-06-05 bom(s) updated. 3d models added.
    [HAT.csv, HAT.kicad_sch, designators.csv, positions.csv]
2024-06-10 PCB updated to V0.4.1
    -improvements in holes for audio amplifier
    [HAT.kicad_pcb]
2024-06-10 made opamp in design optional
    [HAT.kicad_sch]
2024-06-10 PCB V0.4.2 finished
    - added OPAMP bypass
    [HAT.kicad_pcb, HAT.kicad_sch]
2024-06-17 Fixed Capacitor schematic error
    [HAT.kicad_pcb, HAT.kicad_sch]
2024-06-17 added LEDboard to code
2024-06-18 Cleanup and added readme.md
    [Functionele specificaties HAT.xlsx, HAT.kicad_pcb, Technische specificaties HAT.xlsx, designators.csv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]
